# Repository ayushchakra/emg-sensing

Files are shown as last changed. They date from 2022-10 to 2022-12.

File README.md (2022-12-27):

# EMG Sensing Circuit Board

Electromygraphy is a medical tool used to evaluate the health of individual muscles and
the nerve cells that dictate their movement. The intention of this project was to design a
four-channel surface electromygraphy (sEMG) printed circuit board in order to process
real-time electromyographic signals generated from a user’s muscle movements. The
board was intended to communicate with a user’s computer via Bluetooth and Serial
to provide flexibility to the physical setup, along with portability for ease of access to
EMG information. The full hardware and software overview can be found [here](https://github.com/ayushchakra/emg-sensing/blob/main/EMG_sensing_final.pdf).

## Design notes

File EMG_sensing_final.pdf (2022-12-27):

## Surface Eletromyography Sensing Board

Ayush Chakraborty, Rucha Dave, and Jiayuan Liu

December 18, 2022

## 1 Introduction

Electromygraphy is a medical tool used to evaluate the health of individual muscles and the nerve cells that dictate their movement. The intention of this project was to design a four-channel surface electromygraphy (sEMG) printed circuit board in order to process real-time electromyographic signals generated from a user’s muscle movements. The board was intended to communicate with a user’s computer via Bluetooth and Serial to provide flexibility to the physical setup, along with portability for ease of access to EMG information. The full hardware and software implementation can be found here. (https://github.com/ayushchakra/emg-sensing)

## 2 Schematic Design

When creating the schematic for our EMG board, we researched various circuit designs that fit within both our budget and the scope of the project. We discussed the benefits of each, seeking guidance from our professor, before finalizing the circuit shown in Figure 1 below.

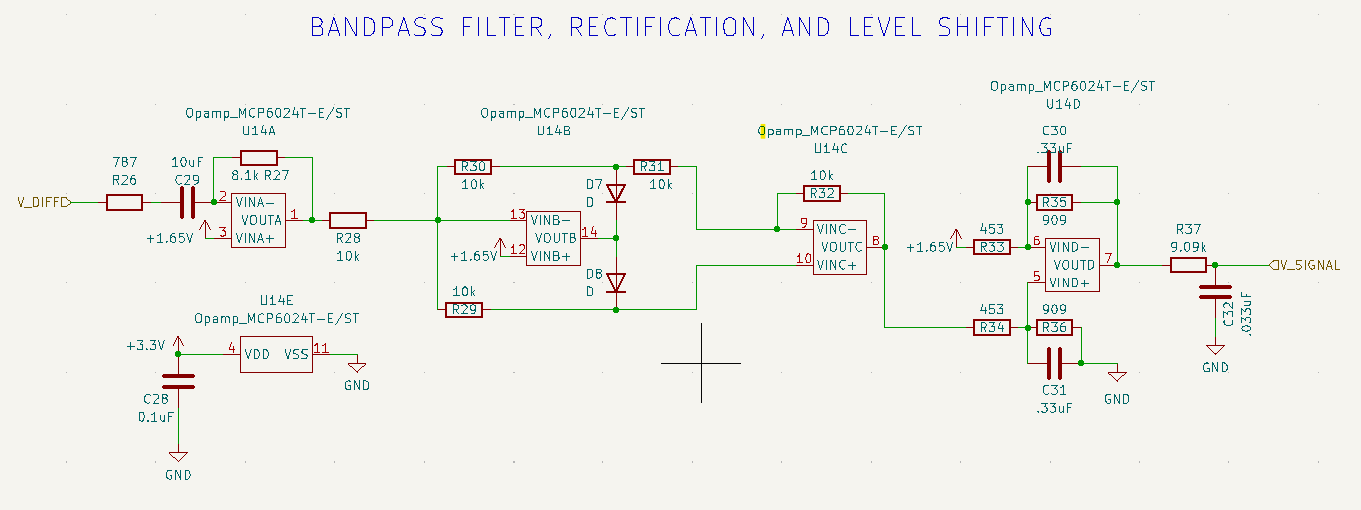
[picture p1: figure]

Figure 1: Circuit Diagram of Signal Processing for EMG

However, before beginning to process the signal, we need to use a differential amplifier to amplify the difference between the signals received between the two EMG nodes.

This was done by using an instrumentation amplifier chip (In-Amp), shown in Figure 2.

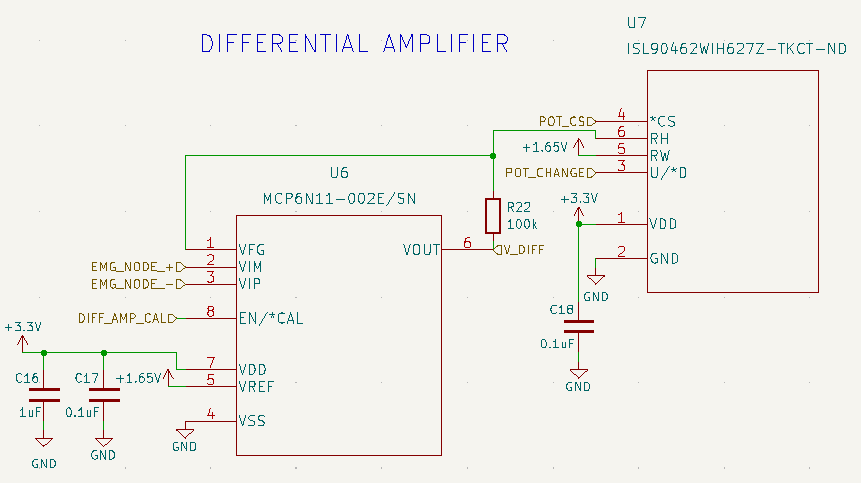
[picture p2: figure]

Figure 2: Circuit Diagram for Differential Amplification for EMG Signals

Starting by just considering one channel, our goal was to process the incoming signal to be normalized against a reference, filtered to remove noise, and then modified to represent a signal the computer could easily analyze. This process involves three steps: high pass filter/amplifier, rectifier, and level shifter/low pass filter/amplifier.

1. High Pass Filter and Amplifier: The first task after receiving a signal from the sensor was to remove noise that had a low frequency (ex: long term decay in signal). The portion of the circuit in Figure 1 furthest to the left depicts this. The cutoff frequency is given by the equation fc =

1
2πRC . Based on this, our
circuit has a high pass cutoff frequency of 20.2 Hz. This means signals below this frequency are removed. Additionally, this portion of the filter also amplifies the signal by 8100
787 , or about 10 times.
2. Rectifier: After low frequency noise was removed from the signal, the signal was rectified to have a reference of 1.65V. This means that, making 1.65V the new "zero" point, all portions of the signal below 1.65V are made "positive". For example, 1.60V would now be 1.70V. The entire signal is now contained between 1.65V and 3.3V without having lost any data. In Figure 1, this is the central portion of the circuit.
3. Level Shifter, Low Pass Filter, and Amplifier: Finally, after having modified the signal, it needed to be put through a low pass filter to remove high frequency noise (background nose or outside interference) and further amplified.

Additionally, it also needed to be re-referenced to 0V to make further analysis easier. The right-most portion of Figure 1’s circuit depicts this process. Here, the low pass filter has a cutoff frequency of fc =

1
2πRC with R = 9.09kΩ and C = 0.033µ F. This makes the cutoff frequency 530 Hz. All frequencies above this are removed from the data. Next, the signal is shifted so that 1.65V moved to 0V. This results in the signal ranging from 0V to 1.65V. Finally, the amplifier is 2x, allowing the signal that originally encompassed only 0 to 1.65V to now double in amplitude and cover the entire range from 0 to 3.3V.

## 3 LTspice Simulation

In order to validate the proposed signal processing system, we decided to simulate the bandpass filter, rectifier, and level shifter in LTspice. To start, we simulated each individual component individually. When running these isolated tests, we were validating the following:

1. The high pass filter and amplifier has a gain of 10 and its characteristic frequency is around 20 Hz.
2. The rectifier properly rectifies the signal with a 1.65V reference.
3. The level shifter, amplifier, and second order low pass filter has a characteristic frequency of 530 Hz and properly shifts the signal to encompass the full 0.0V to 3.3V measurable range.

Once each individual component was validated, they were integrated together to resemble the actual signal processing module. To test the full signalling process, we inputted a wide range of signals, some out of the expected frequency range and some within that range and examined if the output was as expected. Figure 3 depicts an example input-output for a signal with a frequency of 100 Hz and amplitude of 150 mV (which is the highest expected amplitude being inputted to this module). 100 Hz is within the desired frequency and should be amplified. Figure 4 depicts an example input-output for a signal with a frequency of 0.5 Hz and amplitude of 150 mV. 0.5 Hz is outside of the desired frequency and should be filtered.

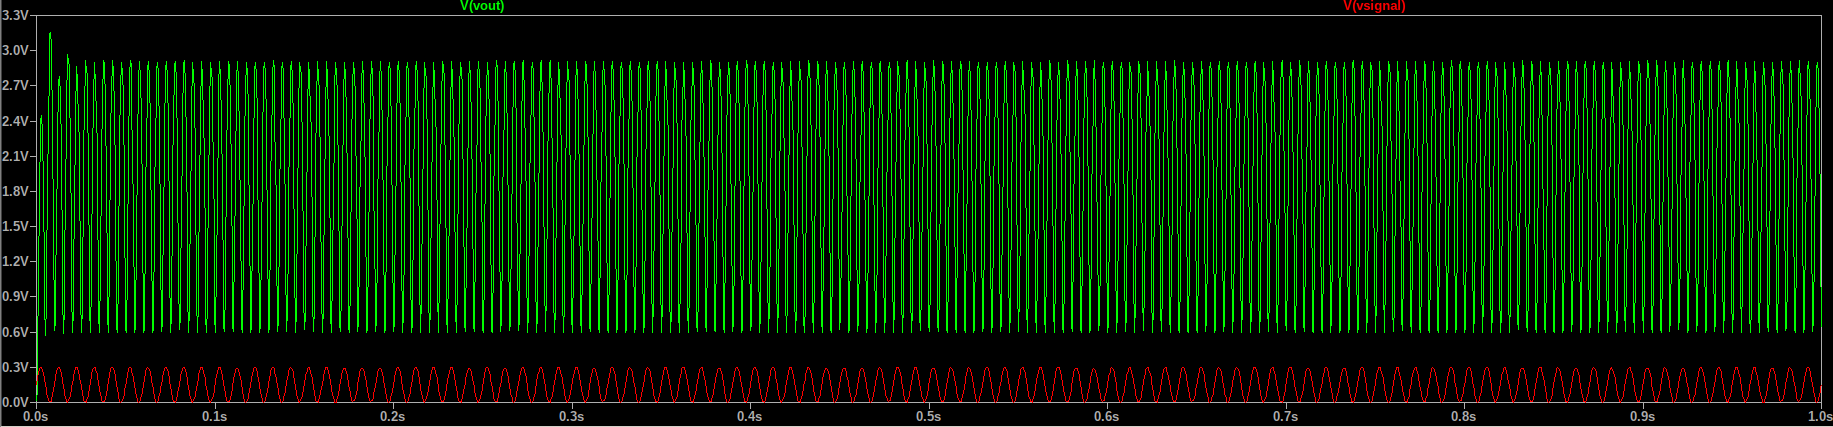
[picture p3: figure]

Figure 3: Simulation of signal processing of signal with frequency within the desired range (100 Hz). Green represents the output signal and red represents the input

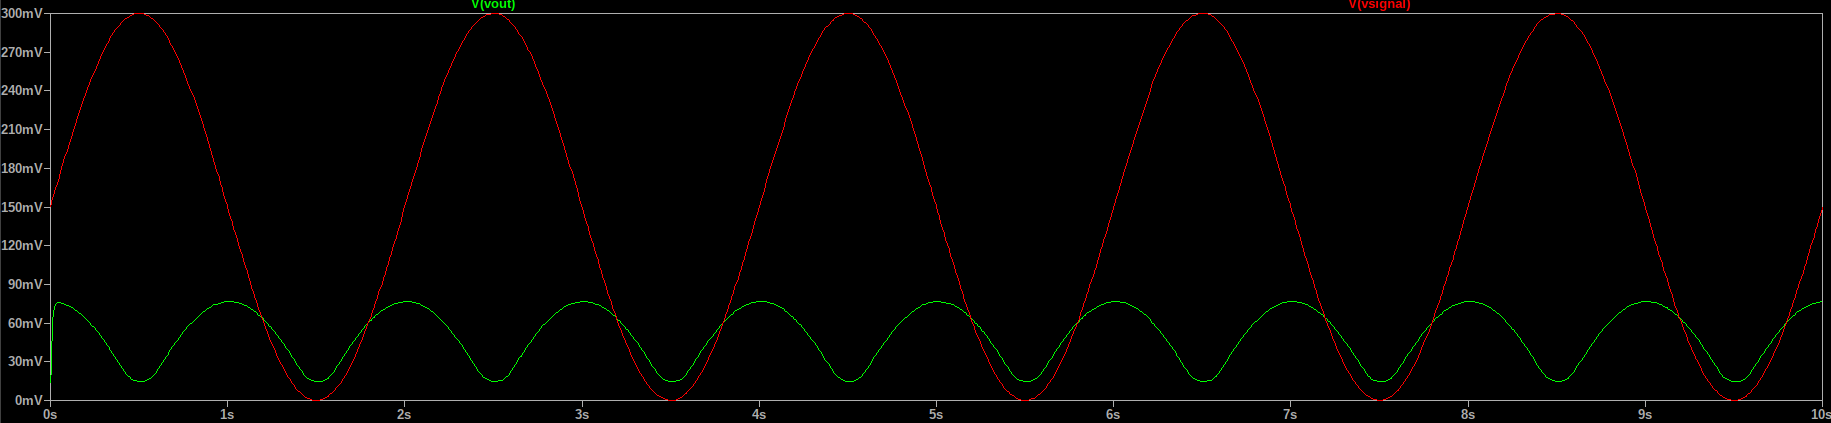
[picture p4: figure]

Figure 4: Simulation of signal processing of signal with frequency outside the desired range (0.5 Hz). Green represents the output signal and red represents the input

Since the simulation behaved as expected for several different inputs that account for the signals we were expecting, we were fairly confident in our schematic design, allowing us to move forward to developing the circuit board layout.

## 4 Additional Parts

Finally, we needed to include numerous additional parts to our board to pull it together for the final purpose. We used multiple bulk and bypass capacitors, a Bluetooth module, RP2040, RP2040 memory device, a potentiometer, etc. These all involved their own circuitry. A complete circuit is given in our GitHub here. (https://github.com/ayushchakra/emg-sensing) A full list of all parts used is provided in Section 6 (Bill of Materials).

## 5 Layout Design

While developing the layout for our EMG sensing board, we had to design it with the following constraints in mind:

1. Minimize the overall area of the board. This allows for the EMG sensing to be as portable as possible.
2. Allow for easy access to the EMG signal input pin headers to minimize disorderly wiring that could interfere with consistent signalling.

While developing, we had two main iterations to the design: one two layer design and, based on received feedback, one four layer design.

### 5.1 Iteration 1 - Two Layer Board

For our first iteration, we planned a two layer board, where the top layer was for power and signals, while the bottom layer was for ground and signal. To start, each footprint was organized into separate component groups, which were power management, each of the four signal processing modules, and the micro controller. Then, they were placed relative to each other, adhering to any specifications on each data sheet (ex: bypass capacitors within 10mm of their corresponding pad, RP2040’s memory device placed as close as possible to the RP2040). This was done without traces to easily shift components, while trying to minimize space to adhere to design constraint 1.

Once organized, each individual component group was placed relative to each other. We chose to place the EMG signal input pin headers on the very bottom edge of the board, all next to each other, for easy access. Then, each individual signal processing group was placed near the corresponding pin headers. The power management module was placed right of these signals, allowing for the shortest path between power and the signalling devices that require power. Finally, the micro controller and other corresponding parts were placed in above the signal processing modules, allowing their output to be routed directly to the RP2040. Then, the traces between each component were routed, starting with the 3.3V power source, then the 1.65V power source, and finally each of the signal lines. This led to a rather messy layout, as can be seen in Figure 5.

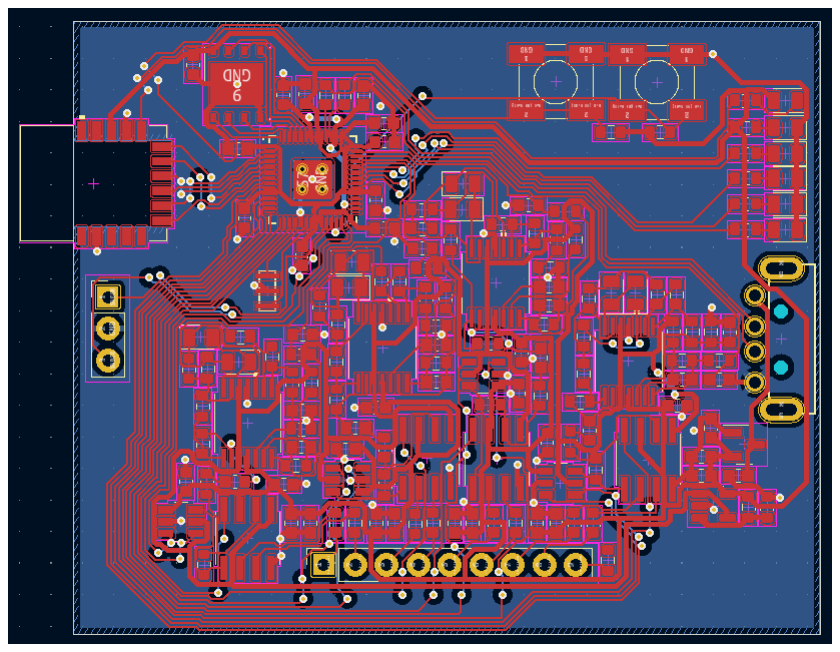
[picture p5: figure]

Figure 5: First Iteration of EMG Board Layout.

The primary concern was that due to the close proximity of the numerous digital signals being routed from the RP2040 to the digital potentiometers and operational amplifiers, there would be significant cross-talk between the lines, causing logical errors when using the board. This become the basis for the next iteration. Another concern was the rather messy power distribution. Since we had to routed +1.65V and +3.3V throughout the signal processing modules, there were significant crosses between the two lines, causing concern about providing consistent power to each integrated circuit component.

### 5.2 Iteration 2 - Four Layer Board

For the second layout design, we chose to implement a four year board, where the board stack up from top to bottom was as follows: power and signal, ground and signal, power, ground and signal. The reason for the third layer containing a power layer was so that the +3.3V could be provided solely through this layer, while only +1.65V would be routed through the top layer, leading to a simpler power distribution.

Additionally, the availability of two additional layers meant that the digital signals from the RP2040 could be more evenly distributed and routed away from each other to preserve signal integrity. In terms of component placement, the placement in the two-layer design was only slightly modified to move components closer together since the top layer required less room for traces. This led to a smaller overall board, better adhering to the first design constraint. The updated layout can be seen in Figure 6.

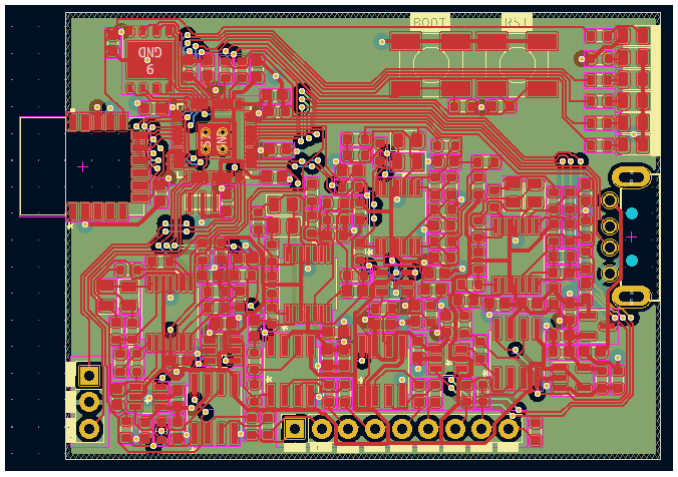
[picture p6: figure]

Figure 6: Second Iteration of EMG Board Layout.

While there were significantly more vias in this design, the presence of extra layers allowed for interruptions of the ground plane to be evenly distributed, allowing us to maintain two relatively continuous ground planes. This served as our final layout design for this revision of the board.

## 6 Bill of Materials

In order to physically create the board, the following components were used (per board):

Component Name | Quantity
0.1µF Capacitor | 22
0.33µF Capacitor | 8
1µF Capacitor | 7
10µF Capacitor | 6
0.033µF Capacitor | 4
10kΩ Resistor | 22
100kΩ Resistor | 13
453Ω Resistor | 8
909Ω Resistor | 8
1kΩ Resistor | 6
787Ω Resistor | 4
8.1kΩ Resistor | 4
9.09kΩ Resistor | 4
5.1kΩ Resistor | 2
27Ω Resistor | 2
Schottky Diode | 8
LED | 6
Differential Amplifier (MCP6N11) | 4
Digital Potentiometer (ISL90462WIH627Z-TKCT-ND) | 4
Quad Operational Amplifier (MCP6024) | 4
Serial Flash Memory (W25Q128JV) | 1
RP2040 | 1
BLE Module (RN4871) | 1
Linear Regulator (MCP1702T) | 1
Single Operational Amplifier (MCP6021) | 1.555
Ceramic Resonator | 1
Buttons | 2
USB A Male Connector | 1
01x09 Male Pin Header | 1
01x03 Male Pin header | 1

Table 1: Bill of Materials

The detailed part sheet, include part references and specific part models, can be found here. (https://docs.google.com/spreadsheets/d/11DgLzIWRdh5BubuOiiBkJtaQQjjR8HkK38gM1tA7Nxc/edit#gid=0)

## 7 Circuit Board Population

We made several attempts before successfully assembled a fully functional PCB board. The biggest challenge in the assembly process came from soldering the RP2040 and the Serial Flash Memory device as they were both QFN packages. For both of the first two boards we populated, we were unable to establish a connection between the RP2040 and a laptop. While debugging the issue, we noticed that the power indicator was flickering rather than maintaining a constant brightness, leading us to believe that there was an issue with our power distribution on the board. Upon further investigation, we found that the voltage output of the linear regulator that stepped the USB 5V input down to 3.3V was inconsistent, oscillating between 0V and 2.3V. It was also reaching significantly high temperatures. Using a thermal camera, we found that there was another elevated thermal area on the RP2040, suggesting that there was a short between two pads. This problem was resolved by reflowing the board and using a soldering iron to remove any new shorts between pads. This allowed us to establish a connection between the RP2040 and a laptop.

Another issue we encountered was, whenever we flashed code on to the RP2040, it immediately reset and became ready for another flash rather than storing the firmware image. This led us to believe that there was an issue with the connection between the RP2040 and the serial flash memory device. While there were no noticeable shorts between the two devices, we decided to re-heat the connections between the two. After doing so and flashing another image, the device was successfully able to store it, resolving the issue.

The second difficulty came from debugging one of the EMG signal channels which outputs a constant high voltage even without any active signal input. To troubleshoot, we simulated voltage at each pin along that trace with LTspice and compared the simulated voltage to the actual voltage measured with an oscilloscope. Eventually, this problem was resolved by replacing the quad op-amp used in the signal processing module for that channel.

## 8 Firmware Overview

For this circuit, the firmware, running on the RP2040, was responsible to analyzing and communicating the current reading of each EMG channel. For the first iteration of the firmware architecture, we had two main requirements for the first iteration.

1. Continuously read the input of 4 analog signals (processed EMG signals).
2. Send the read values of each EMG channel, along with a marker to denote which channel it came from, via the USB connection.

To program the RP2040, we chose to use the arduino-pico library, (https://arduino-pico.readthedocs.io/en/latest/) which is a hardware abstraction library for the RP2040 that allows it to be programmed using the Arduino IDE. The firmware was split into two main functions, setup() and loop().

The setup() function begins by initializing 4 indicator LEDs to HIGH. This is to make sure any firmware image flashed to the RP2040 is properly running on the micrcontroller. Then, the USB serial connection is begun as a baud rate of 9600 bits per second.

Code Segment 1

int serial_baud_rate = 9600; int LED_PIN_ONE = 8;
int LED_PIN_TWO = 9;
int LED_PIN_THREE = 10;
int LED_PIN_FOUR = 11;

void setup() {
pinMode(14, OUTPUT);
digitalWrite(14, HIGH);
pinMode(15, OUTPUT);
digitalWrite(15, HIGH);
pinMode(18, OUTPUT);
digitalWrite(18, HIGH);
pinMode(23, OUTPUT);
digitalWrite(23, HIGH);
pinMode(LED_PIN_ONE, OUTPUT); digitalWrite(LED_PIN_ONE, HIGH); pinMode(LED_PIN_TWO, OUTPUT); digitalWrite(LED_PIN_TWO, HIGH); pinMode(LED_PIN_THREE, OUTPUT); digitalWrite(LED_PIN_THREE, HIGH); pinMode(LED_PIN_FOUR, OUTPUT); digitalWrite(LED_PIN_FOUR, HIGH); Serial.begin(serial_baud_rate);
}

Next, the loop() function, which is continuously called, serves the purpose of reading each analog signal from the 4 EMG channels and sending it over serial. The addition of x0000 to each signal is to serve as the marker for which channel the signal came from. This is for the software to differentiate between signals. This means that each message takes is composed of the left most digit indicating the channel number and the next four digits indicated the 10 bit reading from the analog pin (0-1024). Once sent, the serial interface is flushed to ensure that the messages are sent.

Code Segment 2

void loop() {
Serial.println(analogRead(A0) + 10000); Serial.println(analogRead(A1) + 20000); Serial.println(analogRead(A2) + 30000); Serial.println(analogRead(A3) + 40000); Serial.flush();
delay(.5);
}

## 9 Software Overview

The first iteration of the software, which would interface with the EMG sensing board via serial, was split into two main functions: initialize_serial() and process_serial_input().

The initialize_serial() was designed to establish the serial connection with the hardware. This is done using python’s serial (https://pyserial.readthedocs.io/en/latest/) library, where we specified a USB port, serial baud rate, and timeout in order to establish the connection.

Code Segment 3

def initialize_serial():
arduino_port = "/dev/ttyACM0"
baud_rate = 9600
serial_port = serial.Serial(arduino_port, baud_rate, timeout=1) return serial_port

Once established, the process_serial_input() is called in order to continuously process data on the serial line and dynamically updated a graph with the received data. Each received line is decoded, then the first digit is split off to determine which EMG channel the data should be appended to. Then, the analog reading is extracted and appended to a list of received values for the channel. Additionally, we record the time that each message was received.. The received time was used instead of the time that the message was processed on the microcontroller in order to minimize the amount of data being sent via the serial line, allowing for a higher rate of EMG values. The data processing is nested in a try-except statement due to errors that arise from bitloss in serial communication.

Code Segment 4

while True:
try:
curr_data = int(serial_port.readline().decode()) data[curr_data//10000][1].append(curr_data%10000) data[curr_data//10000][0].append(time.perf_counter()-start_time)
except (UnicodeDecodeError, ValueError, KeyError):
continue

In order to plot the data, a graph with four subplots, one for each channel, is initialized. Then, each sub-graph is assigned a line to store its data. On every iteration of the while loop, those lines are updated based on the received data. Finally, the x axis is set to visualize the most recent ten seconds of data.

Code Segment 3

plt.ion()
fig = plt.figure()
ax1 = fig.add_subplot(111) ax2 = fig.add_subplot(222) ax3 = fig.add_subplot(223)
ax4 = fig.add_subplot(224)

line1, = ax1.plot(data[1][0], data[1][1], ’k-’) line2, = ax2.plot(data[2][0], data[2][1], ’g-’) line3, = ax3.plot(data[3][0], data[3][1], ’b-’) line4, = ax4.plot(data[4][0], data[4][1], ’r-’)

while True:
# Process serial input

line1.set_xdata(data[1][0]) line1.set_ydata(data[1][1]) line2.set_xdata(data[2][0]) line2.set_ydata(data[2][1]) line3.set_xdata(data[3][0]) line3.set_ydata(data[3][1]) line4.set_xdata(data[4][0]) line4.set_ydata(data[4][1])

ax1.set_xbound(lower=data[1][0][-1]-10, upper=data[1][0][-1]+10) ax2.set_xbound(lower=data[1][0][-1]-10, upper=data[1][0][-1]+10) ax3.set_xbound(lower=data[1][0][-1]-10, upper=data[1][0][-1]+10) ax4.set_xbound(lower=data[1][0][-1]-10, upper=data[1][0][-1]+10)

fig.canvas.draw()
fig.canvas.flush_events()

An example plot is shown in Figure 7.

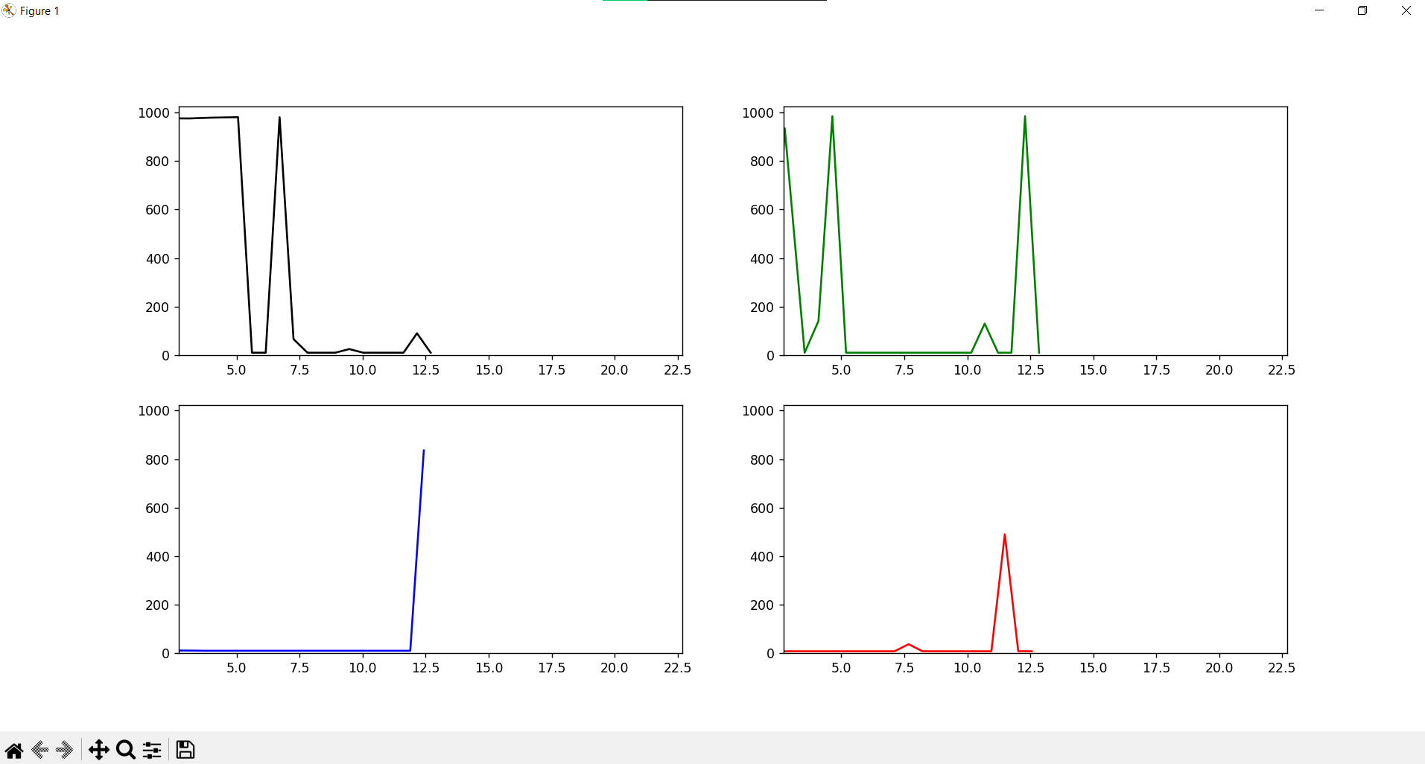
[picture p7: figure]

Figure 7: Sample visualization generated by a user’s laptop while running an EMG trial.

## 10 Results

With the current hardware, we have received inconsistent results in processing and analyzing EMG data from the sensing board. At times, we are able to properly receive data. This is demonstrated in our one-channel demo. (https://www.youtube.com/watch?v=9YESAbq6-Ng) However, there are issues with running all four channels working synchronously. During some tests, all four channels can be properly monitored for a brief period of time, but, in most tests, only one or two channels yield expected results while the others constantly remain undetectable. The full demo of the current state of the system can be found here. (https://youtu.be/dAzlrd0NfQ0)

### 10.1 Limitations

Possible causes of the inconsistent functioning of all channel include:

1. Misplacement of the EMG electrodes on the muscle. If the electrodes are placed improperly, they may pick up the same signal, causing their difference to be always be 0, leading to no signal.
2. Inadequate contact between the EMG electrode and the muscle. If proper contact isn’t established with the muscle, then the signal will be weaker, or not detectable at all, leading to improper results.
3. Delay in serial communication. We found that, at times, there is a delay between a physical movement and the visualization of that response. We believe this is either because of how the serial communication is implemented or a physical limit to how fast serial communication can be established.

These problems might have resulted in the board not being able to accurately detect every muscle movement on all four channels.

## 11 Reflection

### 11.1 Ayush

This project was an excellent learning experience for me. It was my first hardware project that wasn’t firmly scaffolded by external design constraints, allowing me to explore new avenues in electrical engineering. This included learning a lot about setting my own design constraints based on a specific function I want to implement. The main challenge I faced during this project was learning how to debug an embedded system. Numerous times throughout the process, I wasn’t sure if there was a hardware or software issue causing unintended results, which forced me to learn new debugging tools to isolate the problem to one or the other and act accordingly.

Additionally, this project taught me the value of implementing features to de-risk certain aspects of the project in order to maximize the chance of meeting an intended deliverable. For example, we wanted to establish a bluetooth connection between the sensing board and a computer, but due to time constraints, were not able to implement this. Thankfully, we had de-risked the bluetooth communication by also including a serial interface to receive data, allowing us to still extract and visualize the processed EMG signal.

### 11.2 Rucha

Coming into this class, I had a very minimal understanding of how circuit components that we had learned about in ISIM could be brought together to accomplish a goal. Through this final project, I was really able to delve deep into different filters and amplifier designs to understand the basics of how a signal could be processed to reach the final goal. This project not only helped me strengthen my conceptual understanding of the different circuit portions change a signal, but also gave me a chance to mathematically step my way through the circuit and analyze it. I really enjoyed this project and believe I learned a lot from the process.

### 11.3 Jiayuan

I learned a lot from the technical aspect of this project, especially in designing signal processing circuit with operational amplifiers, board population, and board debugging. The main challenge I met in the circuit designing stage was analyzing the different filters we researched. Some of the confusions I had in the schematics designing stage were cleared later while debugging the board with an oscilloscope, as I physically measure the voltage at each pin of the filters. Overall, I found this project challenging and engaging.

## 12 Next Steps

To address the problems we had with inconsistent signal measurement, our next step is to try using one electrode as the reference while placing the other electrode on the center of a muscle, instead of placing a electrodes pair on one muscle. To develop more meaningful features of our board, we can first improve our software for faster data reading and add on algorithm for muscle movement classification. This project can potentially become a interactive game for user to exercise different part muscles!

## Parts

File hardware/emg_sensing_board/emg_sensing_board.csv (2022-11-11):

Source: | /Users/Ayush/Documents/GitHub/emg-sensing/kicad/EMG_sensing_draft/EMG_sensing_draft.kicad_sch
Date: | Friday, November 11, 2022 at 01:10:32 AM
Tool: | Eeschema (6.0.9-0)
Generator: | /Applications/KiCad/KiCad.app/Contents/SharedSupport/plugins/bom_csv_grouped_by_value_with_fp.py
Component Count: | 155
Ref | Qnty | Value | Cmp name | Footprint | Description | Vendor
C1, C3, C12, C13, C18, C19, C26, C29, C34, C35, C36, | 11 | 1uF | C | Capacitor_SMD:C_0603_1608Metric | Unpolarized capacitor
C2, C4, C5, C6, C7, C8, C9, C10, C11, C14, C15, C16, C17, C20, C21, C23, C24, C27, C30, C37, C38, C39, | 22 | 0.1uF | C | Capacitor_SMD:C_0603_1608Metric | Unpolarized capacitor
C22, C25, C28, C40, C41, C42, | 6 | 10uF | C | Capacitor_SMD:C_0603_1608Metric | Unpolarized capacitor
C31, C32, C43, C44, C45, C46, C47, C48, | 8 | .33uF | C | Capacitor_SMD:C_0603_1608Metric | Unpolarized capacitor
C33, C49, C50, C51, | 4 | .033uF | C | Capacitor_SMD:C_0603_1608Metric | Unpolarized capacitor
D1, D2, D3, D4, D5, | 5 | LED | LED | LED_SMD:LED_0805_2012Metric | Light emitting diode
D6, | 1 | PWR | LED_Filled | LED_SMD:LED_0805_2012Metric | Light emitting diode, filled shape
D7, D8, D9, D10, D11, D12, D13, D14, | 8 | D | D |  | Diode
J1, | 1 | USB_A_0480370001 | USB_A_0480370001 | Eclectronics:USB_A_0480370001
J2, | 1 | EMG_SIGNAL | Conn_01x03 | Connector_PinHeader_2.54mm:PinHeader_1x03_P2.54mm_Vertical | Generic connector, single row, 01x03, script generated (kicad-library-utils/schlib/autogen/connector/)
J3, | 1 | DEBUG | Conn_01x03 | Connector_PinHeader_2.54mm:PinHeader_1x03_P2.54mm_Vertical | Generic connector, single row, 01x03, script generated (kicad-library-utils/schlib/autogen/connector/)
R1, R2, | 2 | 5.1k | R | Resistor_SMD:R_0603_1608Metric | Resistor
R3, R4, | 2 | 27 | R | Resistor_SMD:R_0603_1608Metric | Resistor
R5, R6, R11, R12, R25, R26, R27, | 7 | 100k | R | Resistor_SMD:R_0603_1608Metric | Resistor
R7, R8, R9, R10, R13, R14, | 6 | 1k | R | Resistor_SMD:R_0603_1608Metric | Resistor
R15, R32, R33, R34, | 4 | 787 | R | Resistor_SMD:R_0603_1608Metric | Resistor
R16, R17, R18, R20, R21, R24, R30, R35, R36, R38, R41, R42, R43, R44, R47, R48, R51, R54, R55, R62, R64, R65, | 22 | 10k | R | Resistor_SMD:R_0603_1608Metric | Resistor
R19, R37, R39, R40, | 4 | 8.1k | R | Resistor_SMD:R_0603_1608Metric | Resistor
R22, R23, R45, R46, R49, R50, R52, R53, | 8 | 453 | R | Resistor_SMD:R_0603_1608Metric | Resistor
R28, R29, R56, R57, R58, R59, R60, R61, | 8 | 909 | R | Resistor_SMD:R_0603_1608Metric | Resistor
R31, R63, R66, R67, | 4 | 9.09k | R | Resistor_SMD:R_0603_1608Metric | Resistor
S1, | 1 | RST | SW | Eclectronics:TL3301AFxxxxJ
S2, | 1 | BOOT | SW | Eclectronics:TL3301AFxxxxJ
U1, U2, U7, U8, | 4 | MCP6N11-002E/SN | MCP6N11-002E{slash}SN | MCP6N11:MCP6N11-002ESN
U3, | 1 | W25Q128JV | W25Q128JV | Package_SON:WSON-8-1EP_6x5mm_P1.27mm_EP3.4x4.3mm
U4, U5, U10, U12, | 4 | ISL90462WIH627Z-TKCT-ND | ISL90462WIH627Z-TKCT-ND | ISL90462WIH627Z:ISL90462WIH627Z-TKCT-ND
U6, | 1 | RP2040 | RP2040 | Eclectronics:RP2040
U9, | 1 | RN4871-I/RM140 | RN4871-I{slash}RM140 | RN4871:RN4871
U11, | 1 | MCP1702T-3302E_CB | MCP1702T-3302E_CB | Package_TO_SOT_SMD:SOT-23
U13, U15, U16, U17, | 4 | Opamp_MCP6024T-E/ST | Opamp_MCP6024T-E{slash}ST_4 | MCP6024:MCP6024T
U14, | 1 | MCP6021 | MCP6021 | Package_TO_SOT_SMD:SOT-23-5
Y1, | 1 | 12MHz | Crystal | Eclectronics:CSTNE

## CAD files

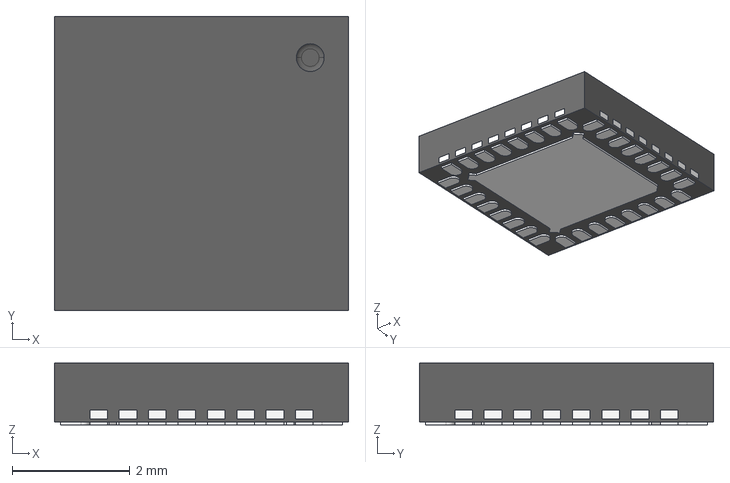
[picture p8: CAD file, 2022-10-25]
hardware/Eclectronics/3dshapes/QFN-32_5x5.stp
5.00 x 5.00 x 1.05 mm

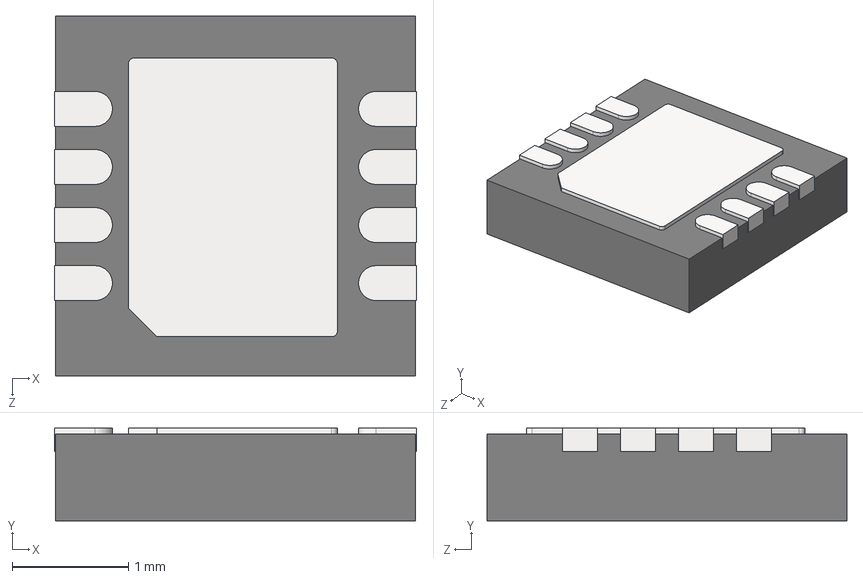
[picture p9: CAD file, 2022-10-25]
hardware/Eclectronics/3dshapes/DFN-8-3x3-0_5.STEP
3.12 x 0.8 x 3.10 mm
User Library-My-DFN-8-3x3-0.5_Part 11
User Library-My-DFN-8-3x3-0.5_Body
User Library-My-DFN-8-3x3-0.5_14
User Library-My-DFN-8-3x3-0.5_13
User Library-My-DFN-8-3x3-0.5_2
User Library-My-DFN-8-3x3-0.5_1
User Library-My-DFN-8-3x3-0.5_11
User Library-My-DFN-8-3x3-0.5_3
User Library-My-DFN-8-3x3-0.5_12
User Library-My-DFN-8-3x3-0.5_4
User Library-My-DFN-8-3x3-0.5_TP

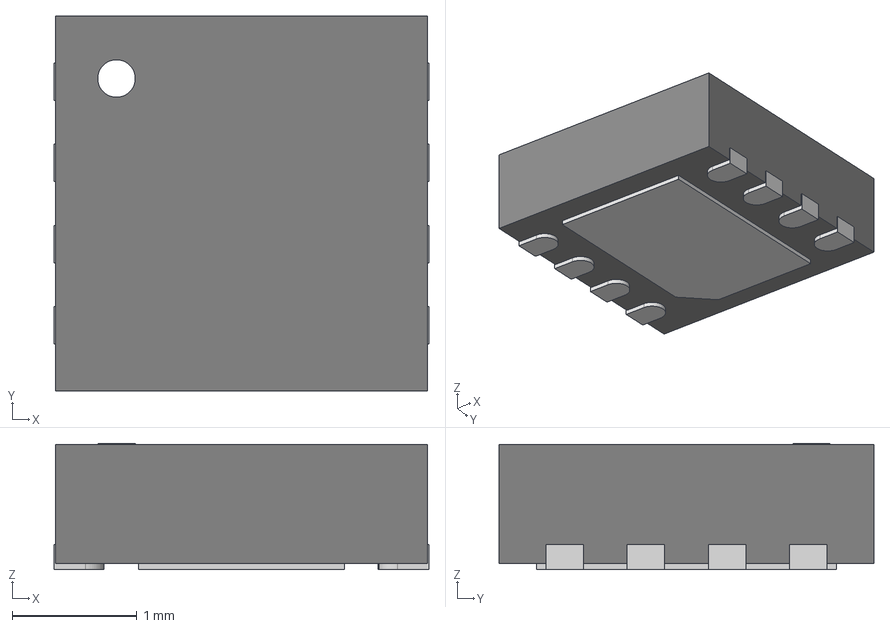
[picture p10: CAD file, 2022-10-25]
hardware/Eclectronics/3dshapes/DFN8_3x3_0.65.step
3.00 x 3.00 x 1.01 mm

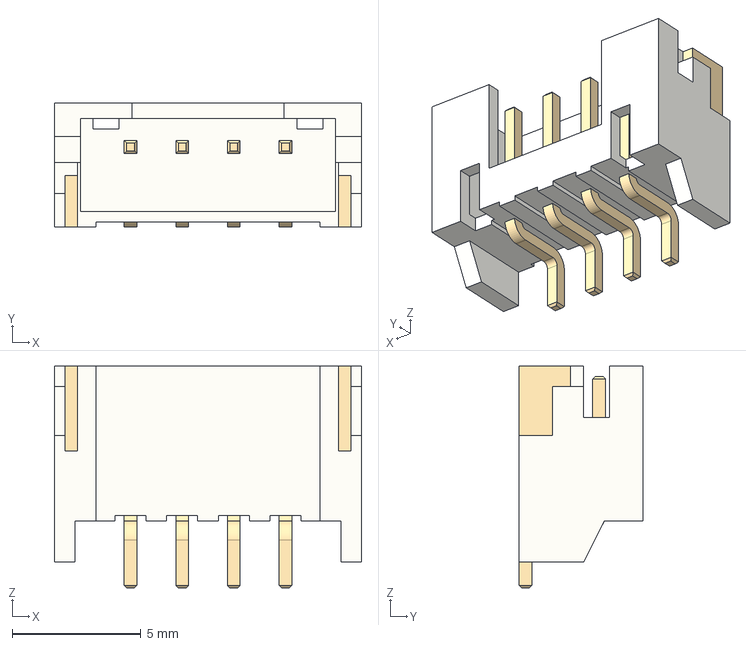
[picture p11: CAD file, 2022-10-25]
hardware/Eclectronics/3dshapes/S4B-PH-SM4-TB.stp
11.9 x 4.80 x 8.60 mm

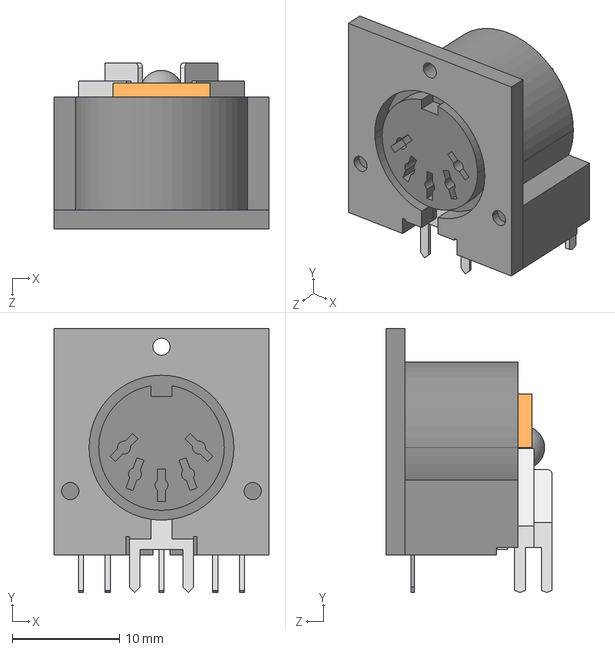
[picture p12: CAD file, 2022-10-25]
hardware/Eclectronics/3dshapes/CUI_SDS-50J.step
20.0 x 24.6 x 15.5 mm

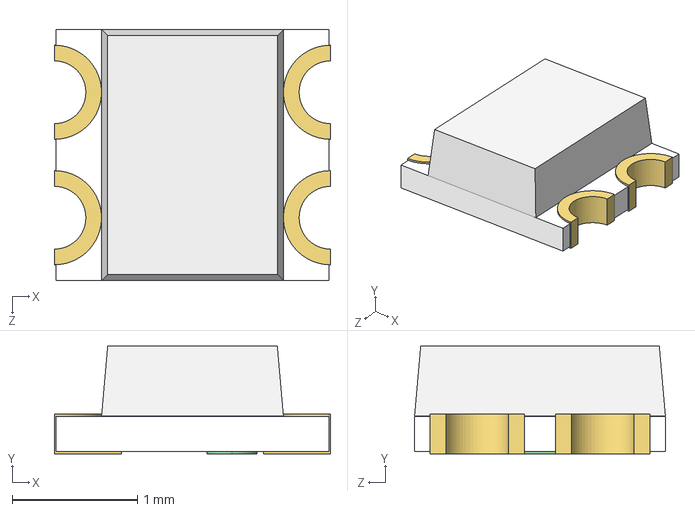
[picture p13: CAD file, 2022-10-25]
hardware/Eclectronics/3dshapes/WS2812-2020.STEP
2.20 x 0.86 x 2.00 mm

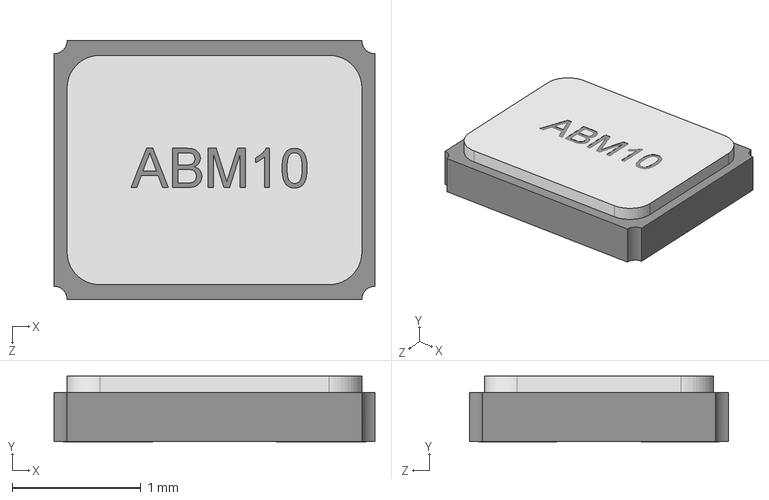
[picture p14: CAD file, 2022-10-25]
hardware/Eclectronics/3dshapes/ABM10.STP
2.49 x 0.508 x 2.01 mm

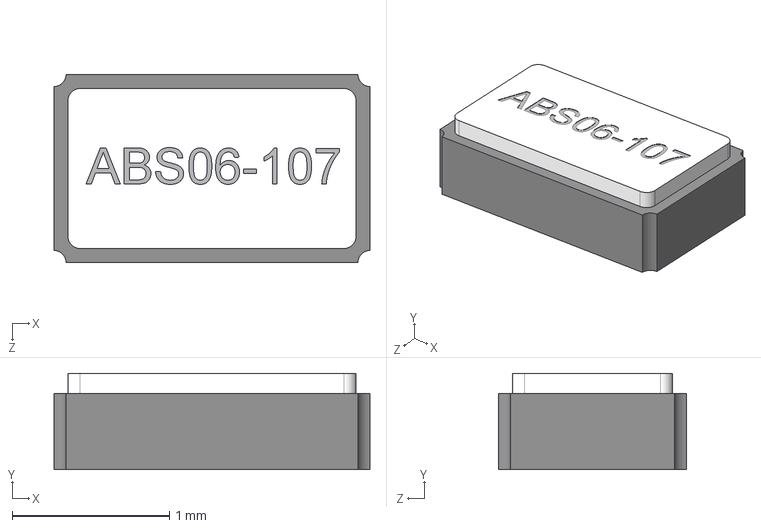
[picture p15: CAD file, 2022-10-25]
hardware/Eclectronics/3dshapes/ABS06-107.STP
2.01 x 0.612 x 1.19 mm

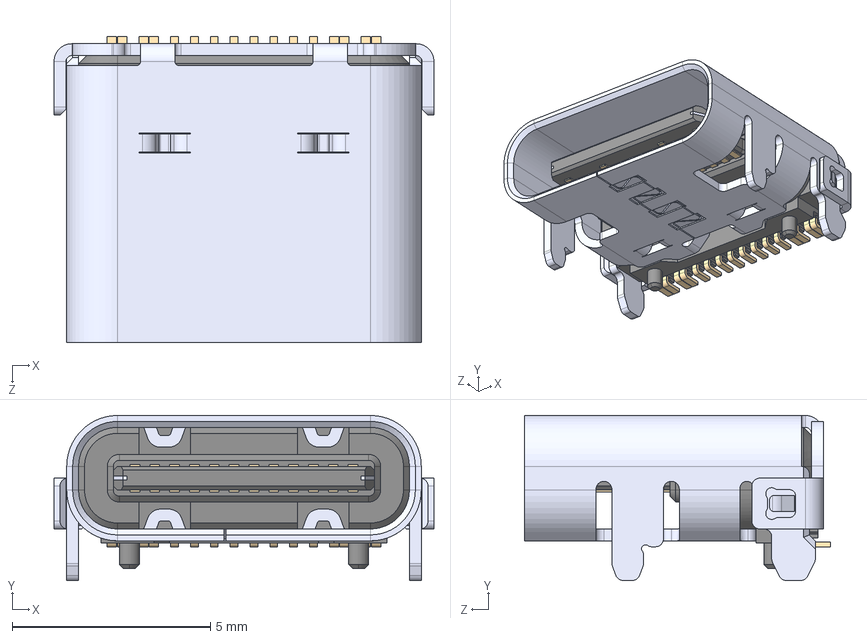
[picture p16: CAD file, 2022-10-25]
hardware/Eclectronics/3dshapes/USB4105-GF-A.step
9.58 x 4.16 x 7.71 mm

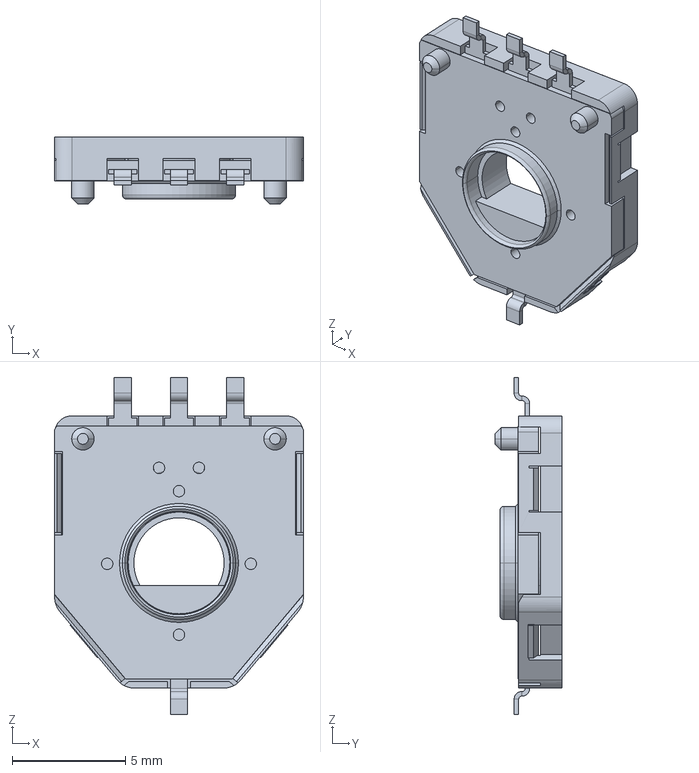
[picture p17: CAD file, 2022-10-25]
hardware/Eclectronics/3dshapes/3382g-001-xxx.stp
11.0 x 2.95 x 14.9 mm

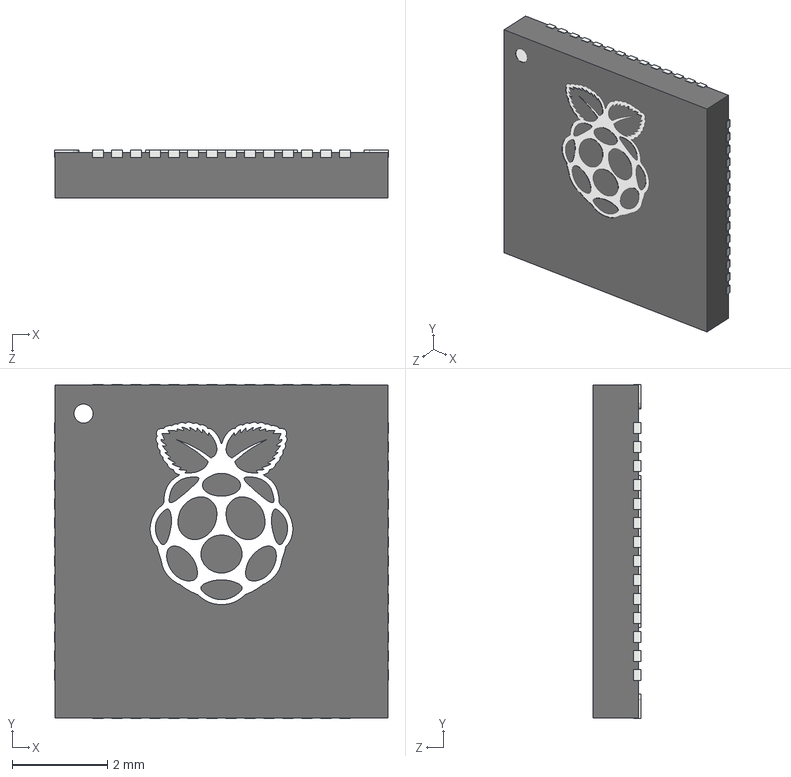
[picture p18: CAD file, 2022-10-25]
hardware/Eclectronics/3dshapes/RP2040_QFN_PACKAGE.STEP
7.02 x 7.02 x 1.00 mm

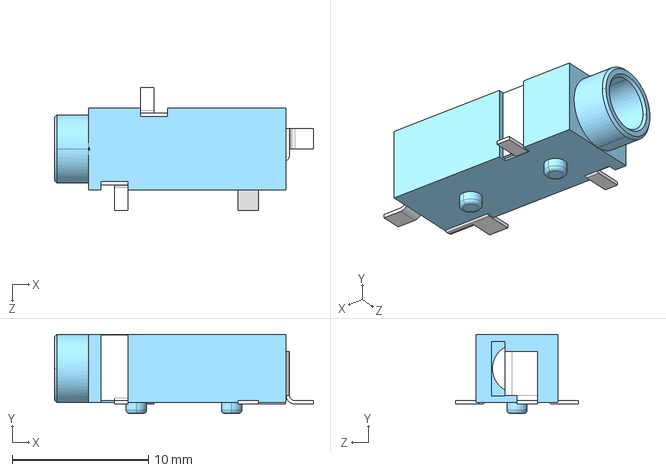
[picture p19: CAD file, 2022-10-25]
hardware/Eclectronics/3dshapes/SJ-3524-SMT-TR-BE.step
19.0 x 5.80 x 9.00 mm

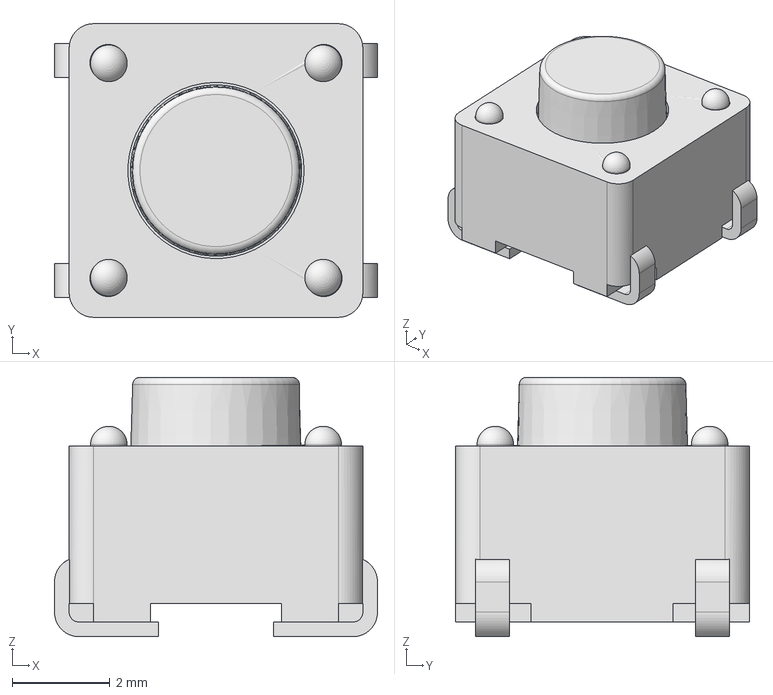
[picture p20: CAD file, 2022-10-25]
hardware/Eclectronics/3dshapes/TL3301AFxxxxJ.stp
6.60 x 6.00 x 5.30 mm

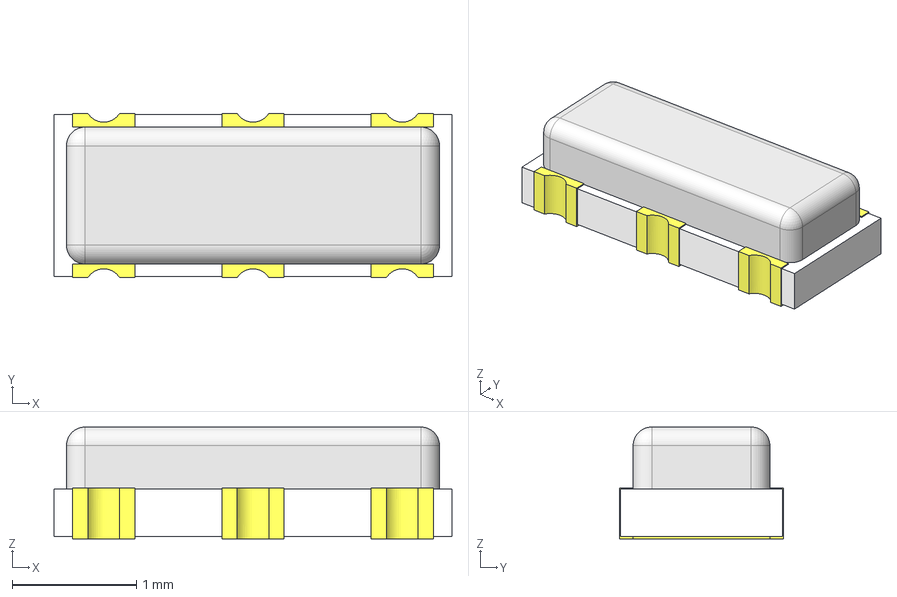
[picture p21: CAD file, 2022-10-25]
hardware/Eclectronics/3dshapes/CSTNE.step
3.20 x 1.32 x 0.9 mm

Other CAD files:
hardware/Eclectronics/3dshapes/WS2812_RGB_LED_updated.stp
hardware/Eclectronics/3dshapes/RNR0011A.stp
hardware/Eclectronics/3dshapes/PA5003.182NLT.step
hardware/Eclectronics/3dshapes/TL3301NFxxxxJ.stp
hardware/Eclectronics/3dshapes/KXT321LHS.stp
hardware/Eclectronics/3dshapes/UFQFPN48.stp
hardware/Eclectronics/3dshapes/WSON8-6x5.STEP

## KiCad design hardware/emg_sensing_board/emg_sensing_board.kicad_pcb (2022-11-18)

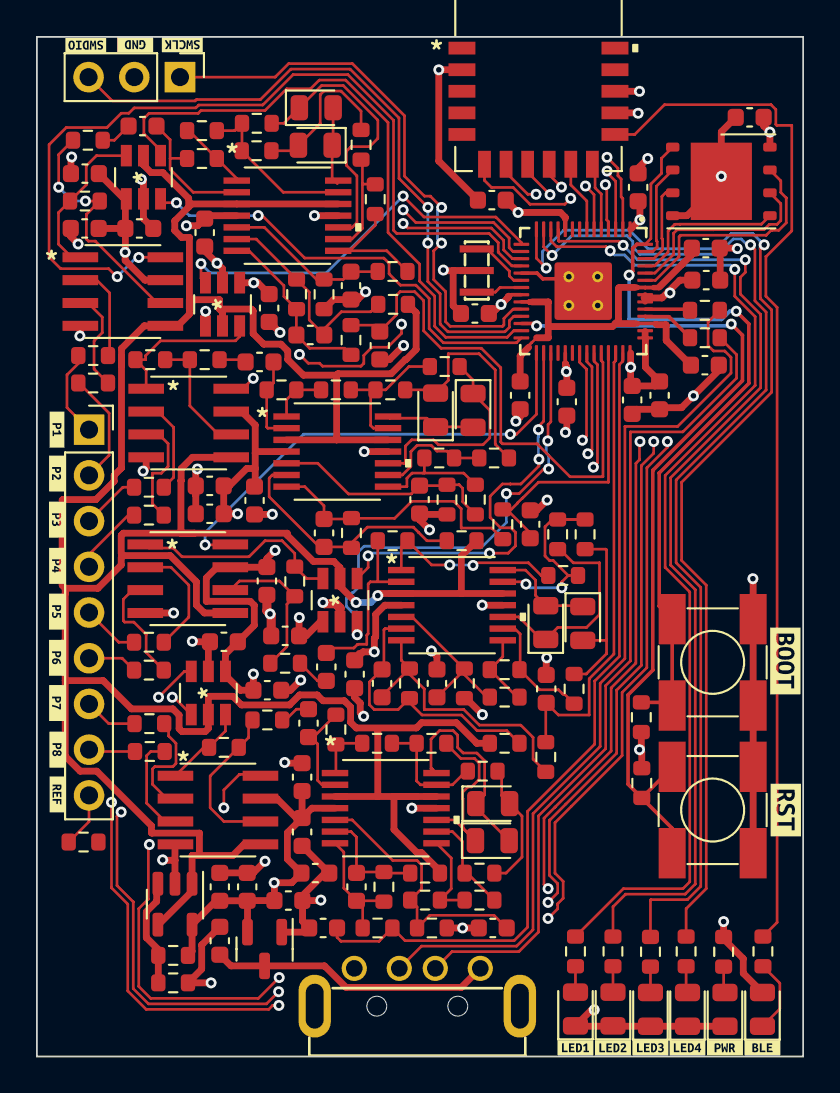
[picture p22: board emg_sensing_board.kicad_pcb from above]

Board: 4 copper layers, 42.6 x 56.6 mm, 177 parts (0 on the bottom side), 127 nets.

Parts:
C1, C2, C3, C4, C16, C17, C32: 1uF; C_0603_1608Metric
C5, C6, C7, C8, C9, C10, C11, C12, C13, C14, C15, C18, C19, C20, C21, C22, C23, C26, C27, C29, C33, C43: 0.1uF; C_0603_1608Metric
C24, C25, C28, C30, C31, C44: 10uF; C_0603_1608Metric
C34, C35, C36, C37, C38, C39, C45, C46: .33uF; C_0603_1608Metric
C40, C41, C42, C47: .033uF; C_0603_1608Metric
D1, D2, D3, D4, D5: LED; LED_0805_2012Metric
D6: PWR; LED_0805_2012Metric
D7, D8, D9, D10, D11, D12, D13, D14: D; D_0805_2012Metric
J1: USB_A_0480370001
J2: Conn_01x09; PinSocket_1x09_P2.54mm_Vertical
J3: DEBUG; PinHeader_1x03_P2.54mm_Vertical
R1, R2: 5.1k; R_0603_1608Metric
R3, R4: 27; R_0603_1608Metric
R5, R6, R7, R8, R32, R33, R34, R35, R36, R37, R38, R39, R40: 100k; R_0603_1608Metric
R9, R10, R11, R12, R13, R14: 1k; R_0603_1608Metric
R15, R16, R17, R62: 787; R_0603_1608Metric
R18, R19, R23, R24, R25, R26, R27, R28, R29, R30, R31, R41, R42, R43, R44, R45, R46, R64, R65, R66, R67, R68: 10k; R_0603_1608Metric
R20, R21, R22, R63: 8.1k; R_0603_1608Metric
R47, R48, R49, R50, R51, R52, R69, R70: 453; R_0603_1608Metric
R53, R54, R55, R56, R57, R58, R71, R72: 909; R_0603_1608Metric
R59, R60, R61, R73: 9.09k; R_0603_1608Metric
S1: RST; TL3301AFxxxxJ
S2: BOOT; TL3301AFxxxxJ
U1, U2, U3, U5: MCP6N11-002E/SN; MCP6N11-002ESN
U4: W25Q128JV; WSON-8-1EP_6x5mm_P1.27mm_EP3.4x4.3mm
U6, U7, U8, U9: ISL90462WIH627Z-TKCT-ND
U10: RP2040
U11: RN4871-I/RM140; RN4871
U12: MCP1702T-3302E_CB; SOT-23
U13, U14, U15, U17: Opamp_MCP6024T-E/ST; MCP6024T
U16: MCP6021; SOT-23-5
Y1: 12MHz; CSTNE
kibuzzard-63775D6F: G***; kibuzzard-63775D6F
kibuzzard-63775D95: G***; kibuzzard-63775D95
kibuzzard-63775DA9: G***; kibuzzard-63775DA9
kibuzzard-63775DCC: G***; kibuzzard-63775DCC
kibuzzard-63775DF3: G***; kibuzzard-63775DF3
kibuzzard-63775E2B: G***; kibuzzard-63775E2B
kibuzzard-63775E08: G***; kibuzzard-63775E08
kibuzzard-63775E55: G***; kibuzzard-63775E55
kibuzzard-63775E69: G***; kibuzzard-63775E69
kibuzzard-63775E81: G***; kibuzzard-63775E81
kibuzzard-63775ECF: G***; kibuzzard-63775ECF
kibuzzard-63775F9D: G***; kibuzzard-63775F9D
kibuzzard-63775F11: G***; kibuzzard-63775F11
kibuzzard-63775F30: G***; kibuzzard-63775F30
kibuzzard-63775F41: G***; kibuzzard-63775F41
kibuzzard-63775F53: G***; kibuzzard-63775F53
kibuzzard-63775FC8: G***; kibuzzard-63775FC8
kibuzzard-63775FF7: G***; kibuzzard-63775FF7
kibuzzard-6377605B: G***; kibuzzard-6377605B
kibuzzard-63776016: G***; kibuzzard-63776016

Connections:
+1.65V: R47.1, R49.1, R51.1, R69.1, U1.5 (VREF), U2.5 (VREF), U3.5 (VREF), U5.5 (VREF), U6.5 (RW), U7.5 (RW), U8.5 (RW), U9.5 (RW), U13.3 (VINA+), U13.12 (VINB+), U14.3 (VINA+), U14.12 (VINB+), U15.3 (VINA+), U15.12 (VINB+), U16.1, U16.4, U17.3 (VINA+), U17.12 (VINB+)
+3.3V: C1.1, C2.1, C3.1, C4.1, C5.2, C6.1, C7.1, C8.1, C9.1, C10.1, C11.1, C12.1, C13.1, C14.1, C15.1, C16.1, C20.1, C21.1, C22.1, C23.1, C25.1, C26.2, C27.2, C29.2, C32.1, C33.1, C43.2, D5.2 (A), R1.2, R2.2, R14.1, R18.1, U1.7 (VDD), U2.7 (VDD), U3.7 (VDD), U4.8 (VDD), U5.7 (VDD), U6.1 (VDD), U7.1 (VDD), U8.1 (VDD), U9.1 (VDD), U10.1 (IOVDD), U10.10 (IOVDD), U10.22 (IOVDD), U10.33 (IOVDD), U10.42 (IOVDD), U10.43 (ADC_AVDD), U10.44 (VREG_VIN), U10.48 (USB_VDD), U10.49 (IOVDD), U11.14 (VBAT), U12.2 (VOUT), U13.4 (VDD), U14.4 (VDD), U15.4 (VDD), U16.5, U17.4 (VDD)
/BLE_RX: U10.2 (GPIO0), U11.7 (UART_RX)
/BLE_TX: U10.3 (GPIO1), U11.8 (UART_TX)
/CTS: U10.5 (GPIO3), U11.11 (P0_0)
/DIF_AMP_FOUR_CAL: U3.8 (EN/*CAL), U10.35 (GPIO23)
/DIF_AMP_ONE_CAL: U1.8 (EN/*CAL), U10.18 (GPIO15)
/DIF_AMP_THREE_CAL: U5.8 (EN/*CAL), U10.29 (GPIO18)
/DIF_AMP_TWO_CAL: U2.8 (EN/*CAL), U10.17 (GPIO14)
/EMG_NODE_EIGHT: R39.2, U3.3 (VIP)
/EMG_NODE_FIVE: R36.2, U5.2 (VIM)
/EMG_NODE_FOUR: R35.2, U2.3 (VIP)
/EMG_NODE_ONE: R32.2, U1.2 (VIM)
/EMG_NODE_SEVEN: R38.2, U3.2 (VIM)
/EMG_NODE_SIX: R37.2, U5.3 (VIP)
/EMG_NODE_THREE: R34.2, U2.2 (VIM)
/EMG_NODE_TWO: R33.2, U1.3 (VIP)
/POT_CHANGE_FOUR: U8.3 (U/*D), U10.37 (GPIO25)
/POT_CHANGE_ONE: U6.3 (U/*D), U10.28 (GPIO17)
/POT_CHANGE_THREE: U9.3 (U/*D), U10.31 (GPIO20)
/POT_CHANGE_TWO: U7.3 (U/*D), U10.15 (GPIO12)
/POT_CS_FOUR: U8.4 (*CS), U10.36 (GPIO24)
/POT_CS_ONE: U6.4 (*CS), U10.27 (GPIO16)
/POT_CS_THREE: U9.4 (*CS), U10.30 (GPIO19)
/POT_CS_TWO: U7.4 (*CS), U10.16 (GPIO13)
/RST_N: U10.7 (GPIO5), U11.10 (RST_N)
/RTS: U10.4 (GPIO2), U11.9 (P3_6)
/RX_IND: U10.6 (GPIO4), U11.6 (P1_6)
/SWCLK: J3.1, U10.24 (SWCLK)
/SWDIO: J3.3, U10.25 (SWDIO)
/USB_D+: J1.3 (D+), R4.2
/USB_D-: J1.2 (D-), R3.1
/V_DIFF_FOUR: R7.1, R62.1, U3.6 (VOUT)
/V_DIFF_ONE: R5.1, R15.1, U1.6 (VOUT)
/V_DIFF_THREE: R8.1, R16.1, U5.6 (VOUT)
/V_DIFF_TWO: R6.1, R17.1, U2.6 (VOUT)
/V_SIGNAL_FOUR: C47.1, R73.2, U10.41 (GPIO29/ADC3)
/V_SIGNAL_ONE: C40.1, R59.2, U10.38 (GPIO26/ADC0)
/V_SIGNAL_THREE: C41.1, R60.2, U10.40 (GPIO28/ADC2)
/V_SIGNAL_TWO: C42.1, R61.2, U10.39 (GPIO27/ADC1)
GND: C1.2, C2.2, C3.2, C4.2, C5.1, C6.2, C7.2, C8.2, C9.2, C10.2, C11.2, C12.2, C13.2, C14.2, C15.2, C16.2, C17.2, C18.2, C19.2, C20.2, C21.2, C22.2, C23.2, C24.1, C25.2, C26.1, C27.1, C29.1, C32.2, C33.2, C35.1, C37.1, C39.1, C40.2, C41.2, C42.2, C43.1, C46.1, C47.2, D1.1 (K), D2.1 (K), D3.1 (K), D4.1 (K), D6.1 (K), J1.4 (GND), J3.2, R19.1, R54.1, R56.1, R58.1, R72.1, S1.1, S2.1, U1.4 (VSS), U2.4 (VSS), U3.4 (VSS), U4.4 (GND), U4.9 (EP), U5.4 (VSS), U6.2 (GND), U7.2 (GND), U8.2 (GND), U9.2 (GND), U10.19 (TESTEN), U10.57 (GND), U11.2 (GND), U11.13 (GND), U12.1 (GND), U13.11 (VSS), U14.11 (VSS), U15.11 (VSS), U16.2, U17.11 (VSS), Y1.2
unnamed: C17.1, C18.1, C19.1, U10.23 (DVDD), U10.45 (VREG_VOUT), U10.50 (DVDD)
unnamed: C24.2, J1.1 (VBUS), U12.3 (VIN)
unnamed: C28.1, R15.2
unnamed: C28.2, R20.1, U13.2 (VINA-)
unnamed: C30.1, R16.2
unnamed: C30.2, R21.1, U14.2 (VINA-)
unnamed: C31.1, R17.2
unnamed: C31.2, R22.1, U15.2 (VINA-)
unnamed: C34.1, R47.2, R53.1, U13.6 (VIND-)
unnamed: C34.2, R53.2, R59.1, U13.7 (VOUTD)
unnamed: C35.2, R48.2, R54.2, U13.5 (VIND+)
unnamed: C36.1, R49.2, R55.1, U14.6 (VIND-)
unnamed: C36.2, R55.2, R60.1, U14.7 (VOUTD)
unnamed: C37.2, R50.2, R56.2, U14.5 (VIND+)
unnamed: C38.1, R51.2, R57.1, U15.6 (VIND-)
unnamed: C38.2, R57.2, R61.1, U15.7 (VOUTD)
unnamed: C39.2, R52.2, R58.2, U15.5 (VIND+)
unnamed: C44.1, R62.2
unnamed: C44.2, R63.1, U17.2 (VINA-)
unnamed: C45.1, R69.2, R71.1, U17.6 (VIND-)
unnamed: C45.2, R71.2, R73.1, U17.7 (VOUTD)
unnamed: C46.2, R70.2, R72.2, U17.5 (VIND+)
unnamed: D1.2 (A), R9.2
unnamed: D2.2 (A), R10.2
unnamed: D3.2 (A), R11.2
unnamed: D4.2 (A), R12.2
unnamed: D5.1 (K), R13.2
unnamed: D6.2 (A), R14.2
unnamed: D7.1 (K), D8.2 (A), U13.14 (VOUTB)
unnamed: D7.2 (A), R28.2, R41.1
unnamed: D8.1 (K), R26.2, U13.10 (VINC+)
unnamed: D9.2 (A), R30.2, R42.1
unnamed: D10.1 (K), R27.2, U14.10 (VINC+)
unnamed: D9.1 (K), D10.2 (A), U14.14 (VOUTB)
unnamed: D11.1 (K), D12.2 (A), U15.14 (VOUTB)
unnamed: D11.2 (A), R31.2, R43.1
unnamed: D12.1 (K), R29.2, U15.10 (VINC+)
unnamed: D13.1 (K), D14.2 (A), U17.14 (VOUTB)
unnamed: D13.2 (A), R66.2, R67.1
unnamed: D14.1 (K), R65.2, U17.10 (VINC+)
unnamed: J2.1, R32.1
unnamed: J2.2, R33.1
unnamed: J2.3, R34.1
unnamed: J2.4, R35.1
unnamed: J2.5, R36.1
unnamed: J2.6, R37.1
unnamed: J2.7, R38.1
unnamed: J2.8, R39.1
unnamed: J2.9, R40.1
unnamed: R1.1, S1.2, U10.26 (RUN)
unnamed: R2.1, S2.2, U4.1 (~CS), U10.56 (~QSPI_CS)
unnamed: R3.2, U10.46 (USB_D-)
unnamed: R4.1, U10.47 (USB_D+)
unnamed: R5.2, U1.1 (VFG), U6.6 (RH)
unnamed: R6.2, U2.1 (VFG), U7.6 (RH)
unnamed: R7.2, U3.1 (VFG), U8.6 (RH)
unnamed: R8.2, U5.1 (VFG), U9.6 (RH)
unnamed: R9.1, U10.11 (GPIO8)
unnamed: R10.1, U10.12 (GPIO9)
unnamed: R11.1, U10.13 (GPIO10)
unnamed: R12.1, U10.14 (GPIO11)
unnamed: R13.1, U11.12 (P0_2)
unnamed: R18.2, R19.2, U16.3
unnamed: R20.2, R23.1, U13.1 (VOUTA)
unnamed: R21.2, R24.1, U14.1 (VOUTA)
unnamed: R22.2, R25.1, U15.1 (VOUTA)
unnamed: R23.2, R26.1, R28.1, U13.13 (VINB-)
unnamed: R24.2, R27.1, R30.1, U14.13 (VINB-)
unnamed: R25.2, R29.1, R31.1, U15.13 (VINB-)
unnamed: R41.2, R44.1, U13.9 (VINC-)
unnamed: R42.2, R45.1, U14.9 (VINC-)
unnamed: R43.2, R46.1, U15.9 (VINC-)
unnamed: R44.2, R48.1, U13.8 (VOUTC)
unnamed: R45.2, R50.1, U14.8 (VOUTC)
unnamed: R46.2, R52.1, U15.8 (VOUTC)
unnamed: R63.2, R64.1, U17.1 (VOUTA)
unnamed: R64.2, R65.1, R66.1, U17.13 (VINB-)
unnamed: R67.2, R68.1, U17.9 (VINC-)
unnamed: R68.2, R70.1, U17.8 (VOUTC)
unnamed: U10.20 (XIN), Y1.1
unnamed: U10.21 (XOUT), Y1.3
unnamed: U4.7 (~HOLD/IO3), U10.51 (QSPI_SD3)
unnamed: U4.6 (SCK), U10.52 (QSPI_SCLK)
unnamed: U4.5 (DI/IO0), U10.53 (QSPI_SD0)
unnamed: U4.3 (~WP/IO2), U10.54 (QSPI_SD2)
unnamed: U4.2 (DO/IO1), U10.55 (QSPI_SD1)

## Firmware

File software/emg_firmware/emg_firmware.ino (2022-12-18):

int LED_PIN_ONE = 8;
int LED_PIN_TWO = 9;
int LED_PIN_THREE = 10;
int LED_PIN_FOUR = 11;

void setup() {
  // put your setup code here, to run once:
  pinMode(14, OUTPUT);
  digitalWrite(14, HIGH);
  pinMode(15, OUTPUT);
  digitalWrite(15, HIGH);
  pinMode(18, OUTPUT);
  digitalWrite(18, HIGH);
  pinMode(23, OUTPUT);
  digitalWrite(23, HIGH);
  pinMode(LED_PIN_ONE, OUTPUT);
  digitalWrite(LED_PIN_ONE, HIGH);
  pinMode(LED_PIN_TWO, OUTPUT);
  digitalWrite(LED_PIN_TWO, LOW);
  pinMode(LED_PIN_THREE, OUTPUT);
  digitalWrite(LED_PIN_THREE, HIGH);
  pinMode(LED_PIN_FOUR, OUTPUT);
  digitalWrite(LED_PIN_FOUR, LOW);
  Serial.begin();
  Serial1.setRX(1);
  Serial1.setTX(0);
  Serial1.begin(115200);
}

void loop() {
  // put your main code here, to run repeatedly:
  // digitalWrite(LED_PIN_ONE, !digitalRead(LED_PIN_ONE));
  // digitalWrite(LED_PIN_TWO, !digitalRead(LED_PIN_TWO));
  // digitalWrite(LED_PIN_THREE, !digitalRead(LED_PIN_THREE));
  // digitalWrite(LED_PIN_FOUR, !digitalRead(LED_PIN_FOUR));
  // delay(500);
  Serial.println(analogRead(A0) + 10000);
  // Serial.println(analogRead(A1) + 20000);
  // Serial.println(analogRead(A2) + 30000);
  // Serial.println(analogRead(A3) + 40000);
  Serial.flush();
  delay(.5);
  // Serial1.println('4');
}

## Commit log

2022-10-25 Add kicad schematics draft
    [EMG_sensing_draft.kicad_pcb, EMG_sensing_draft.kicad_sch]
2022-10-25 Add parts folder and components
    [EMG_sensing_draft.kicad_sch]
2022-10-25 added Eclectronics folder
    [3382g-001-xxx.stp, ABM10.STP, ABS06-107.STP, CSTNE.step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]
2022-10-27 added inamp
    [EMG_sensing_draft.kicad_sch]
2022-10-27 Add rp2040 to schematics
    [EMG_sensing_draft.kicad_sch]
2022-10-27 added BLE module and cleaned up schematic
    [EMG_sensing_draft.kicad_sch]
2022-10-28 Add R and C values (please check!)
    [EMG_sensing_draft.kicad_sch]
2022-10-28 updated RC filter characteristic freq
    [EMG_sensing_draft.kicad_sch]
2022-10-28 Updated resistor values
    [EMG_sensing_draft.kicad_sch]
2022-10-28 Update after design review
    [EMG_sensing_draft.kicad_sch]
2022-11-01 Update circuit based on Brad's advice
    [EMG_sensing_draft.kicad_sch]
2022-11-01 Change opamp chip and add bypass
    [EMG_sensing_draft.kicad_sch]
2022-11-01 Fix diode
    [EMG_sensing_draft.kicad_sch]
2022-11-01 Update circuit w new resistor values
    [EMG_sensing_draft.kicad_sch]
2022-11-02 added power symbol and cleaned up schematic
    [EMG_sensing_draft.kicad_sch]
2022-11-02 added level shifter and second order low pass filter
    [EMG_sensing_draft.kicad_sch]
2022-11-02 restructured repo
    [3382g-001-xxx.stp, ABM10.STP, ABS06-107.STP, CSTNE.step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]
2022-11-02 fixed mcp6024 schematic symbol
    [EMG_sensing_draft.kicad_sch]
2022-11-04 added digital potentiometer
    [EMG_sensing_draft.csv, EMG_sensing_draft.kicad_sch]
2022-11-05 Create circuit sims
2022-11-05 Update rectifying circuit
2022-11-06 linked schematic symbols to footprints
    [EMG_sensing_draft.csv, EMG_sensing_draft.kicad_sch]
2022-11-06 fixed rectifier schematic
    [EMG_sensing_draft.kicad_sch]
2022-11-07 added ltspice model for mcp6n11 to filter sim
2022-11-08 Change schematics based on Brad's comments (incomplete)
    [EMG_sensing_draft.kicad_sch]
2022-11-08 fixed ble pin connection
    [EMG_sensing_draft.kicad_sch]
2022-11-08 Add Brad suggestions
    [EMG_sensing_draft.kicad_sch]
2022-11-08 Edited multi-unit component
    [EMG_sensing_draft.kicad_sch]
2022-11-09 fixed ble pins
    [EMG_sensing_draft.kicad_sch]
2022-11-11 updated footprint assignments
    [EMG_sensing_draft.csv, EMG_sensing_draft.kicad_sch]
2022-11-11 added three channels for emg sensing
    [EMG_sensing_draft.kicad_sch]
2022-11-11 cleaned up four channel schematic
    [EMG_sensing_draft.kicad_sch]
2022-11-11 organized parts on layout
    [EMG_sensing_draft.kicad_pcb, EMG_sensing_draft.kicad_sch]
2022-11-15 finished initial layout
    [EMG_sensing_draft.kicad_pcb, EMG_sensing_draft.kicad_sch]
2022-11-15 Fix errors in layout
    [EMG_sensing_draft.kicad_pcb, EMG_sensing_draft.kicad_sch]
2022-11-15 Fix layout issues
    [EMG_sensing_draft.kicad_pcb]
2022-11-16 removed references from silkscreen
    [EMG_sensing_draft.kicad_pcb]
2022-11-17 fixed rn4871 position
    [EMG_sensing_draft.kicad_pcb]
2022-11-17 fixed rn4871 ground fill
    [EMG_sensing_draft.kicad_pcb]
2022-11-18 fixed copper fill
    [EMG_sensing_draft.kicad_pcb]
2022-11-18 removed references
    [EMG_sensing_draft.kicad_pcb]
2022-11-18 finished four layer layout
    [EMG_sensing_draft.kicad_pcb, EMG_sensing_draft.kicad_sch]
2022-11-18 added silkscreen labels and fixed drc issues
    [EMG_sensing_draft.kicad_pcb]
2022-11-18 fixed usb mounting
    [EMG_sensing_draft.kicad_pcb]
2022-11-18 cleaned directory
    [EMG_sensing_draft.kicad_pcb, EMG_sensing_draft.kicad_sch]
2022-12-18 added heirarichal sheets
    [differential_amplifier.kicad_sch, signal_processing.kicad_sch]
2022-12-18 changed main schematic to reference heirarichal sheets
    [EMG_sensing_draft.kicad_sch]
2022-12-18 organized repo
    [3382g-001-xxx.stp, ABM10.STP, ABS06-107.STP, CSTNE.step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]
2022-12-19 updated gain
    [differential_amplifier.kicad_sch, emg_sensing_board.kicad_sch, signal_processing.kicad_sch]

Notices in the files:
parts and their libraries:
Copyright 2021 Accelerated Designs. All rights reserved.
